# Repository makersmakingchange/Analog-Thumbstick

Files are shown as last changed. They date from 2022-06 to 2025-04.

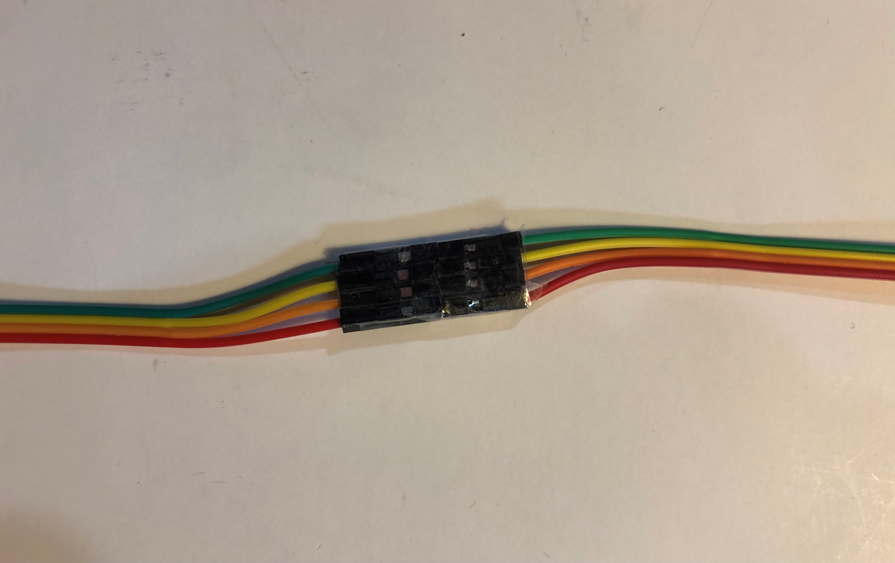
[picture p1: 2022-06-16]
Photos/taped wires.jpg

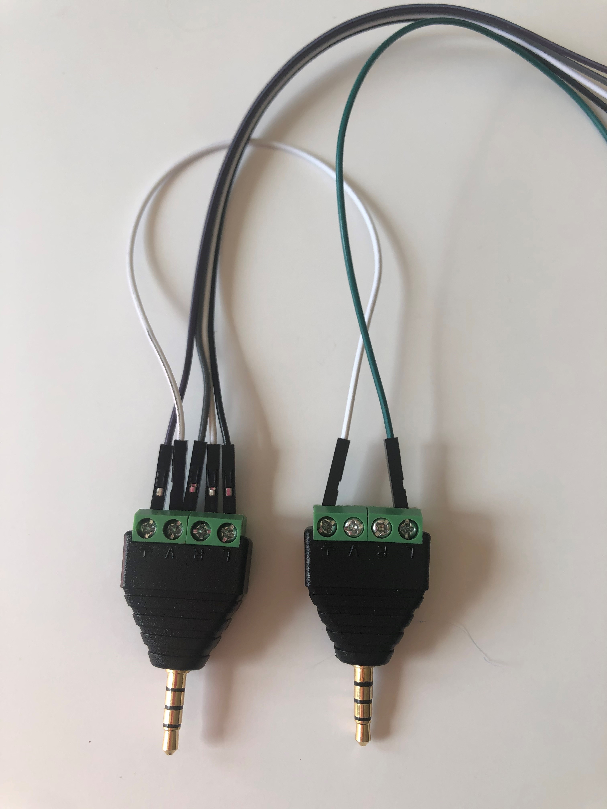
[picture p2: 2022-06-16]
Photos/blue - 2 monojacks.jpg

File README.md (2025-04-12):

# Analog Thumbstick
An analog thumbstick that can be used with the Xbox Adaptive Controller (XAC)



## More info at
- [Makers Making Change Project Page](https://makersmakingchange.com/?post_type=project&p=14952&preview=true)

## Getting Started
1. How to build this device

All of the files and instructions required to build the Low Profile Switch are contained within this repository. Refer to the Maker Checklist below.

2. How to request a build of this device

If you would like to obtain an Analog Joystick but do not have the skills or equipment to do so, you may submit a build request through the [MMC Library Page](https://makersmakingchange.com/project/low-profile-switch/). The requestor is responsible for the cost of materials and any shipping.

3. How to build this device for someone else

If you have the skills and equipment to build this device, and would like to donate your time to create the switch for someone who needs it, visit the [MMC Maker Wanted](https://makersmakingchange.com/maker-wanted/) section.

## Files

### Documentation
| Document             | Version | Link                                                                                  |
|----------------------|---------|---------------------------------------------------------------------------------------|
| Maker Checklist      | 1.0     | [Maker Checklist](/Documentation/Analog_Thumbstick_Maker_Checklist.pdf)         |
| Bill of Materials    | 1.0     | [BOM](/Documentation/Working_Documents/Analog_Thumbstick_BOM.xlsx)                                |
| 3D Printing Guide    | 1.0     | [3D Printing Guide](Documentation/Analog_Thumbstick_3D_Print_Guide.pdf)      |
| Assembly Guide       | 1.0     | [Assembly Guide](/Documentation/Analog_Thumbstick_Assembly_Guide.pdf)           |  
| Design Rationale     | 1.0     | [Design Rationale](/Documentation/Analog_Thumbstick_Design_Rationale.pdf)       |
| User Quick Guide     | 1.0     | [User Guide](/Documentation/Analog_Thumbstick_User_Guide.pdf)                  |

## Attribution 

3D printed joystick housing designed by Kerilyn Kennedy - Makers Making Change, inspired by Ron Nelson.

Documentation created by Neil Squire / Makers Making Change.

## License 
Everything needed or used to design, make, test, or prepare the Low Profile Switch is licensed under the CERN 2.0 Permissive license <https://ohwr.org/project/cernohl/wikis/Documents/CERN-OHL-version-2> (CERN-OHL-P) . 

Accompanying material such as instruction manuals, videos, and other copyrightable works that are useful but not necessary to design, make, test, or prepare the Low Profile Switch are published under a Creative Commons Attribution-ShareAlike 4.0 license <https://creativecommons.org/licenses/by-sa/4.0/> (CC BY-SA 4.0) 

 ----
<!-- ABOUT MMC START -->
## About Makers Making Change
[Makers Making Change Logo](https://www.makersmakingchange.com/)

Makers Making Change is a program of [Neil Squire](https://www.neilsquire.ca/), a Canadian non-profit that uses technology, knowledge, and passion to empower people with disabilities.

Makers Making Change leverages the capacity of community based Makers, Disability Professionals and Volunteers to develop and deliver affordable Open Source Assistive Technologies.

 - Website: [www.MakersMakingChange.com](https://www.makersmakingchange.com/)
 - GitHub: [makersmakingchange](https://github.com/makersmakingchange)
 - Bluesky: [@makersmakingchange.bsky.social](https://bsky.app/profile/makersmakingchange.bsky.social)
 - Instagram: [@makersmakingchange](https://www.instagram.com/makersmakingchange)
 - Facebook: [makersmakechange](https://www.facebook.com/makersmakechange)
 - LinkedIn: [Neil Squire Society](https://www.linkedin.com/company/neil-squire-society/)
 - Thingiverse: [makersmakingchange](https://www.thingiverse.com/makersmakingchange/about)
 - Printables: [MakersMakingChange](https://www.printables.com/@MakersMakingChange)

### Contact Us
For technical questions, to get involved, or to share your experience we encourage you to [visit our website](https://www.makersmakingchange.com/) or [contact us](https://www.makersmakingchange.com/s/contact).
<!-- ABOUT MMC END -->

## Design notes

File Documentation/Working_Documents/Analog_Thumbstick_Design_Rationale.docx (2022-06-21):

# Introduction

There is an identified need for cost-effective analog joysticks that can be used with the Xbox Adaptive Controller (XAC). There are currently not very many commercial joysticks on the market, and the ones that are can be costly. A joystick is required to play several games using the XAC as many users find it too challenging to use 4 switches as the alternative. This joystick is intended to be used with the XAC for anyone who may find it easier to game with a joystick.

# Research

## Commercial Joysticks:

Name | Price | Link | Picture

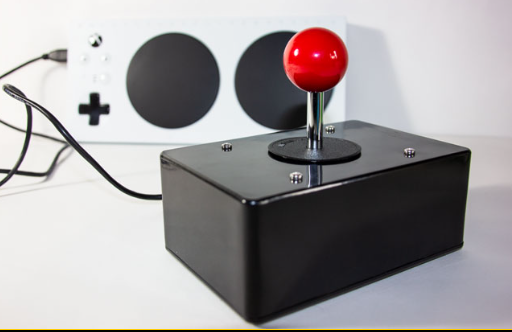
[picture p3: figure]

Ultra-Stik | 95 UK | Accessible Gaming Shop - Ultra-Stik - OneSwitch.org.uk (https://www.oneswitch.org.uk/art.php?id=17)

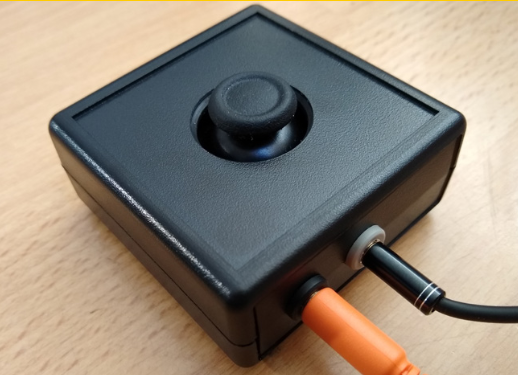
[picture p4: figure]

XAC MINI Stick | 105 UK | XAC Mini Joystick - OneSwitch.org.uk (https://www.oneswitch.org.uk/art.php?id=270)

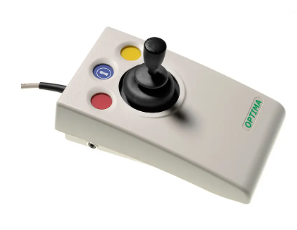
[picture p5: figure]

Optima Joystick | 219.60 UK | Optima Joystick - Video Gaming Assistive Joystick (pretorianuk.com) (https://www.pretorianuk.com/optima-joystick)

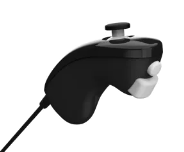
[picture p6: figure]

PDP One-Handed Joystick for Xbox Adaptive Controller | Out of Stock | PDP One-Handed Joystick for Xbox Adaptive Controller (microsoft.com) (https://www.microsoft.com/en-ca/d/pdp-one-handed-joystick-for-the-xbox-adaptive-controller/8qhw8mlwpp1l)
XAC Flat Thumbstick | $74.95 | XAC Flat Thumbstick (evilcontrollers.com) (https://www.evilcontrollers.com/xac-flat-thumbstick)

## DIY Joysticks:

Name | Price | Link | Picture

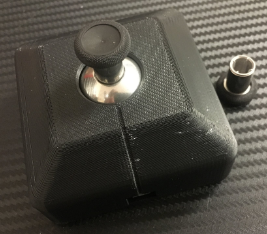
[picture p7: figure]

MINISTIX-TU | $75 | MINISTIX-TU (USB Version) — Warfighter Engaged (https://warfighterengaged.org/shop/ministix-tu)

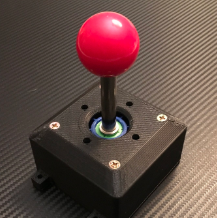
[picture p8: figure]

DPAD-T | $65 | DPAD-T — Warfighter Engaged (https://warfighterengaged.org/shop/dpad-t)

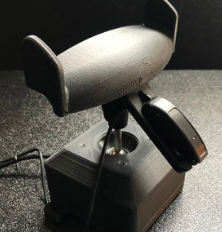
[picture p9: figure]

JOYSTIX-FPS | $75 | JOYSTIX-FPS — Warfighter Engaged (https://warfighterengaged.org/shop/joystix-l-aenef)

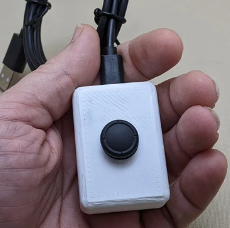
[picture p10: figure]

JoyCon® Style Joystick For XBOX® Adaptive Controller & PC (JoyToKey) | $60.40 | Joycon® Style Joystick for XBOX® Adaptive Controller & PC | Etsy Canada (https://www.etsy.com/ca/listing/1205880837/joycon-style-joystick-for-xbox-adaptive?click_sum=ba40a784&crt=1)

# Requirements

## Goals

G01 | To design a joystick compatible with the Xbox Adaptive Controller.
G02 | That the joystick is cost effective.

## Functional Requirements

F01 | That the joystick could accommodate different shaped toppers.
F02 | The joystick should be able to be used with a low activation force
F03 | Keeping the height of the base of the joystick to a minimum.

# Ideation

## Joystick

The inspiration for this device came from one of Ron Nelson’s joysticks online. The joystick shown below is compatible with the Xbox Adaptive Controller. As you can see, this joystick is mounted in a 3D printed nun chuck shape housing. For this project, it was decided to expand on Ron’s joystick design and design a rectangular 3d printed housing for the joystick so it would be able to lay flat on a surface easier and could potentially be used with Velcro.

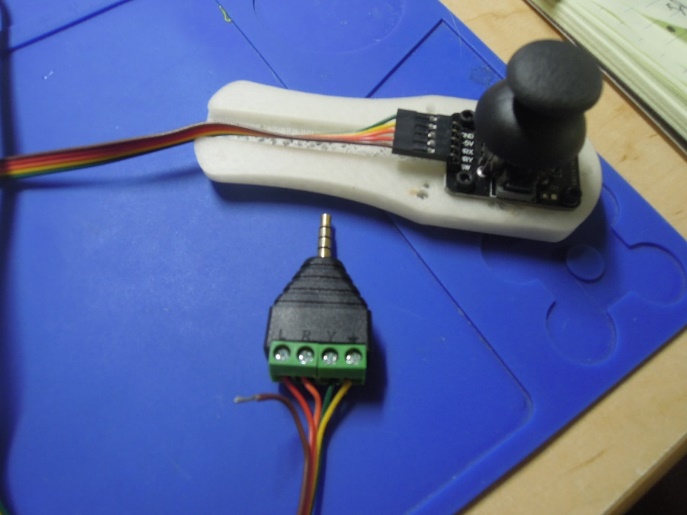
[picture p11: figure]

## Joystick Topper

The inspiration for having a U-shaped topper for the joystick came from one of the participants in our Adaptive Gaming Pilot Project. This participant uses a similar shaped topper on the joystick that operates their wheelchair and thought it would be beneficial to them. They mentioned that the thumbstick topper being used for our joystick would be too small and difficult for them to use. Rather than designing one from scratch, it was thought to modify one that currently exists to fit the required joystick.

# Conceptual Design

## Joystick Housing

The initial concept for the joystick housing was to design a rectangular 3D printed housing to mount the joystick in. It was decided to print the housing in two pieces to eliminate the need for printing with any supports. The two halves are attached together using four #4 1/2” screws – one in each corner. There are walls connecting the screw holes to the outside edge of the housing for reinforcement. Four of the same screws are also used to attach the joystick to the centre of the housing base. The biggest flaw in the first design was that the two walls in the middle of the base that were holding up the joystick snapped off once the joystick was screwed in. This was partially because the screw holes were initially too small, but more likely because there was no support perpendicular to the direction of the wall. The walls were thin and broke very easily when any rotational force was applied.

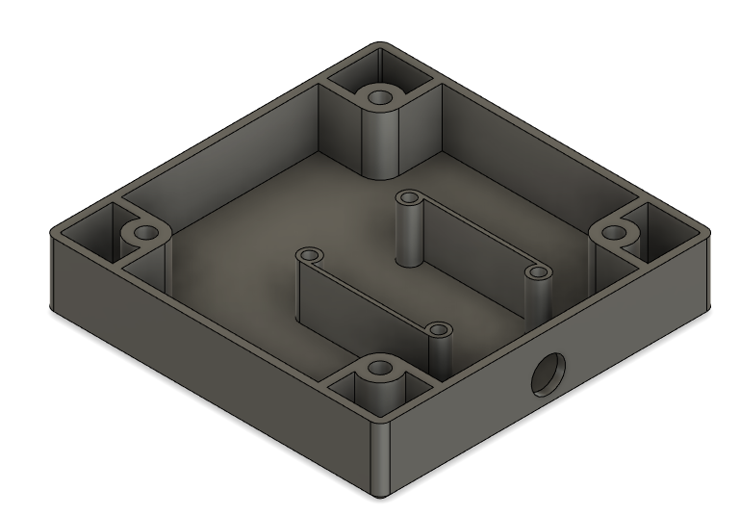
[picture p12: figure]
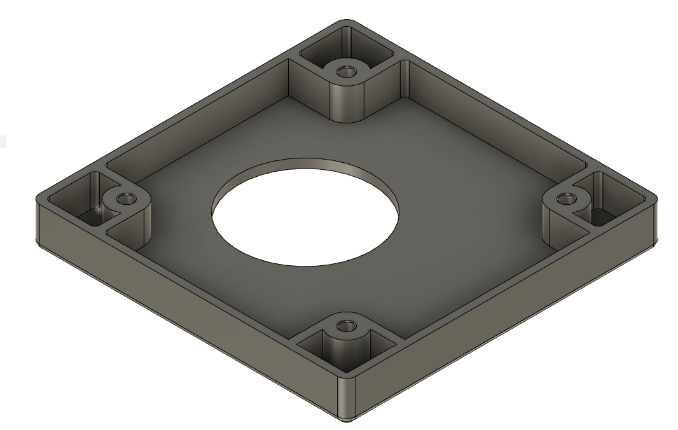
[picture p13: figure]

Bottom | Top (flipped over)

## Joystick Topper

It was thought to modify the joystick topper shown below, which was designed by EgonHeuson. The goal was to modify the base of the topper so that it was compatible with the joystick used.

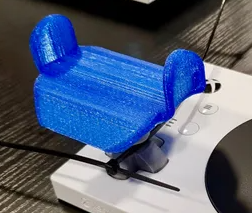
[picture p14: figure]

# Prototyping

Prototyping was used to make sure the joystick was centered with the hole in the top of the housing. Initial prototypes identified that the joystick needed to be slightly moved to achieve this. Prototyping was also used to determine how tall the housing must be to fit the 1/2" screws. Initial prototypes had the screws slightly poking up into the top of the housing, so adjustments were made to fix this. Prototyping was also used to determine an appropriately sized hole in the base for the wires to go through.

# Detailed Design

The analog thumbstick used in this project is compatible with the Xbox Adaptive Controller. There are 2 different versions of the joystick offered: one with the “press down” option (1), and one without (2). The press down function on the joystick is activated by pressing down on the top of the joystick. This function is used in some games, but not most. For this particular joystick, it requires a moderate amount of force to do so. An alternative to using the press down function of the joystick would be to map that function to a different switch. It was decided to offer both versions of the joystick as it is an easy add on if requested by the user.

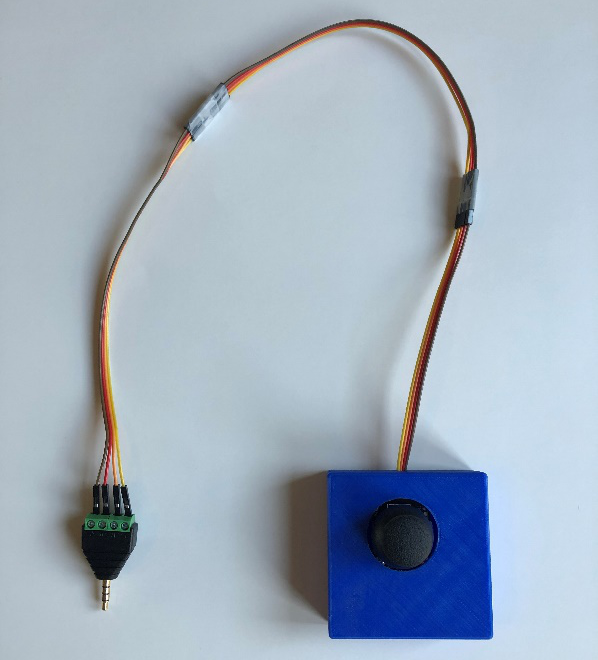
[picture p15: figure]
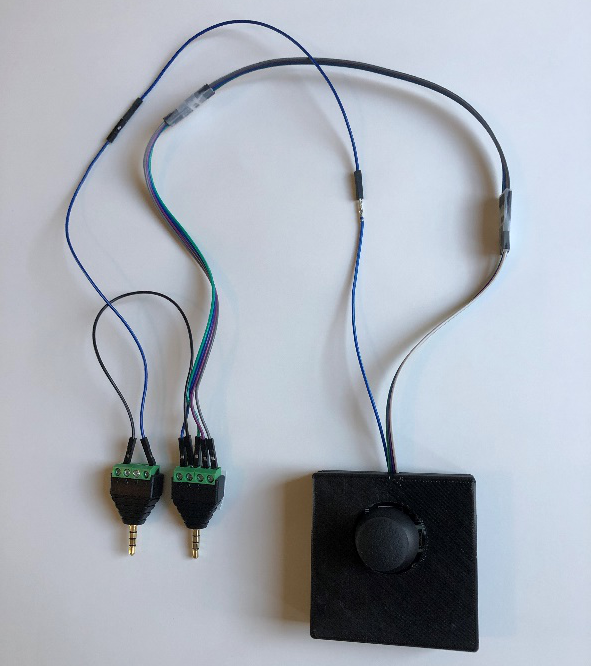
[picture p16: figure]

1. Analog Joystick without Pressdown Feature | 2. Analog Joystick with Pressdown Feature

The housing for the joystick was designed in 2 parts: the top and the base. This model is fairly similar to the enclosure previously described in Concept One. The following were key improvements that were made between iterations of 3D printed enclosures:

- Increasing wall strength where the joystick gets screwed into.
- Optimized the joystick hole size and joystick positioning to align with this hole.
- Modified the height of both 3D printed pieces to work with the 1/2" screws used to hold the enclosure together.

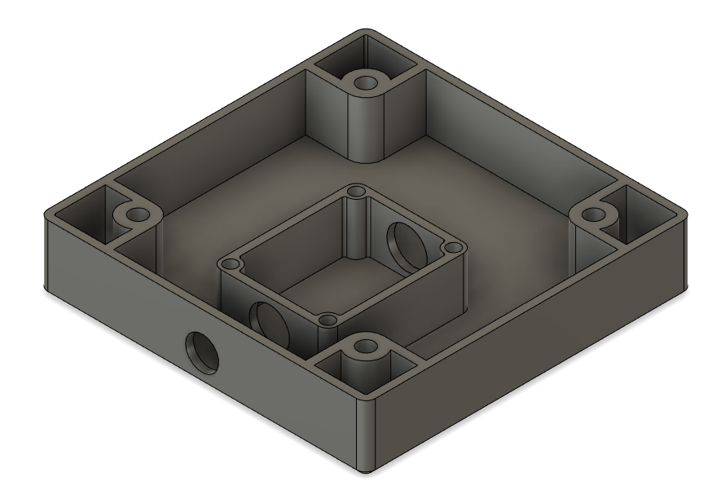
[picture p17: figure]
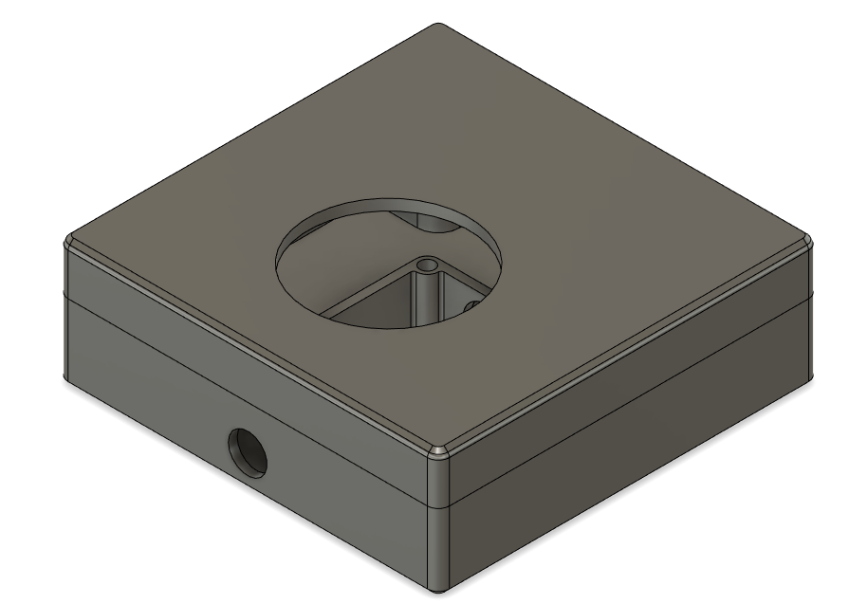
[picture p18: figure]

Bottom | Top

## Joystick Topper

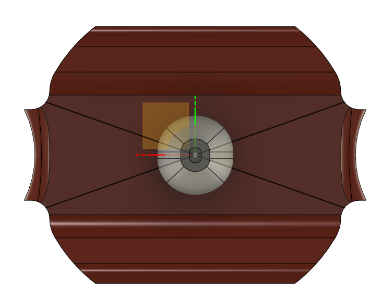
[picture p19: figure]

The U-shaped joystick topper was designed by modifying the base of the original joystick topper by EgonHeuson. The joystick topper was modified by adding a new base to it that would connect to the PS2 joystick used in this project.

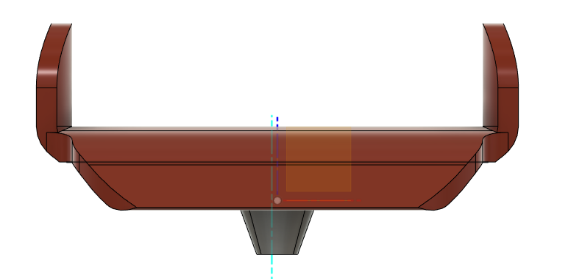
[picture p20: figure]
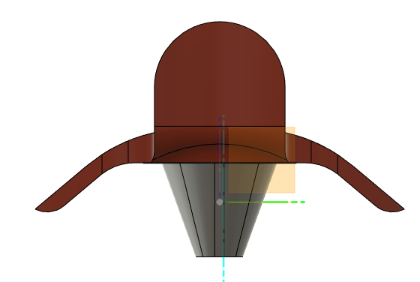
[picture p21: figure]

## Bottom

## Side

## Front

# Testing

The joystick was tested out by plugging it into the Xbox Adaptive Controller and connecting wirelessly to a computer. The online Gamepad Tester (https://gamepad-tester.com/) was used to test all the functions of the joystick. This could also be done by using the Xbox Adaptive controller on a gaming console and using the joystick to navigate the window.

# Opportunities for Improvement

- Minimizing the height of the joystick base.
- Snap fit between joystick top and base.
- Making the base more easily customizable (ex. possibly adding switches right into the base).
- Adding additional joystick toppers.

© 2022 by Neil Squire / Makers Making Change. This work is licensed under the CC BY SA 4.0 License: http://creativecommons.org/licenses/by-sa/4.0 Files available at https://makersmakingchange.com/project/analog-thumbstick/ Page 1 of 1

V1.0 | MAY 2022 Analog Thumbstick Design Rationale

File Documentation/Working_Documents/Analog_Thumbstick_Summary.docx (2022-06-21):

# Title

Analog Thumbstick

## Subtitle

An analog thumbstick that can be used with the Xbox Adaptive Controller (XAC)

## Device Specifications

Build Time:

< 1hr

1-4 hr

5-10hr

>10hr

Cost:

$0 - $10

$11 - $25

$26 - $50

$51 - $100

$101 - $250

$250+

Stage: Recently Added

Skills: Mechanics, 3D Printing

Need: Mobility

Disability: Mobility/Physical

Difficulty: Intermediate

License: Attribution-ShareAlike 4.0 International

Usages: Mobility, Computer Access, Recreation and Leisure

Type: Gaming

Designer: 3D printed joystick housing designed by Kerilyn Kennedy - Makers Making Change, inspired by Ron Nelson.

## Device Details

### Overview

This is a cost-effective analog thumbstick intended to be used for adapted gaming with the Xbox Adaptive Controller (XAC). This device is a more affordable option to commercial thumbsticks on the market. This thumbstick is easy to use and gets plugged into the jacks in the back of the XAC. The design is based on a traditional PS2 thumbstick that is mounted into a 3D printed housing. The original plastic joystick topper can be swapped out for a 3D printed "U" shaped topper to make it easier to use.

### Usage

The Analog Thumbstick is connected to the XAC by plugging the TRRS plug into the "X1 " or " X2" jack on the back of the controller. If so equipped, the optional “push button” feature is connected by plugging into the is enabled on the thumbstick, a second jack will be plugged into the "L" or "R" port that look like joystick icons. The joystick can also be used with the "U" shaped topper. This may be beneficial to someone who may not have the dexterity to use a smaller joystick, or someone who may have limited sensation in their fingers but still has enough wrist movement to use a joystick.

## Compatibility

This joystick is compatible with the Xbox Adaptive controller. The XAC can be used with any Xbox Series X|S or Xbox One, any Windows PC game that supports the Xbox Adaptive Controller, as well as other gaming consoles with an appropriate adapter.

### Cost

The thumbstick costs approximately $30 to build. Note, the device can be built for cheaper if more than one is ordered as several of the parts for this device come in larger quantities than needed for one device.

### Build Instructions

A set of build instructions can be found in the assembly guide that is linked above.

#### Skills Required

- 3D Printing
- Mechanics

#### Time Required

3D Printing Time:

Joystick Housing: 2:47

U-shaped Topper: 4:22

Assembly Time: 10 minutes

#### Tools

- Small Flat Headed Screwdriver
- Tape

#### Components

- 1x Joystick
- 16x Dupont Wires
- 2x Headphone Plugs - only one is needed if the "push button" feature of the joystick is not requested.
- 8x #4 1/2" screws

#### 3D Printing

- Joystick Top
- Joystick Base

All components can be printed with no support at 20% infill with a 0.2mm layer height. 3D print files are linked above.

### Attribution

3D printed joystick housing designed by Kerilyn Kennedy - Makers Making Change, inspired by Ron Nelson.

Documentation created by Neil Squire / Makers Making Change.

© 2022 by Neil Squire / Makers Making Change. This work is licensed under the CC BY SA 4.0 License: http://creativecommons.org/licenses/by-sa/4.0 Files available at https://makersmakingchange.com/project/analog-thumbstick/ Page 1 of 1

V1.0 | MAY 2022 Analog Thumbstick Summary

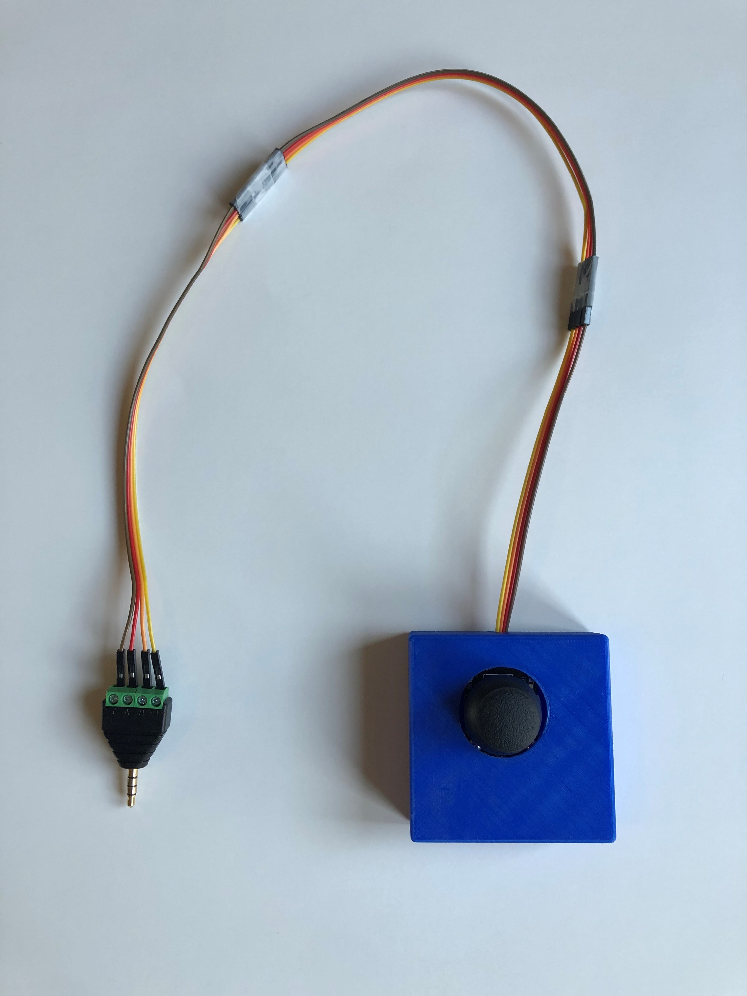
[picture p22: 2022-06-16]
Photos/one mono jack.jpg

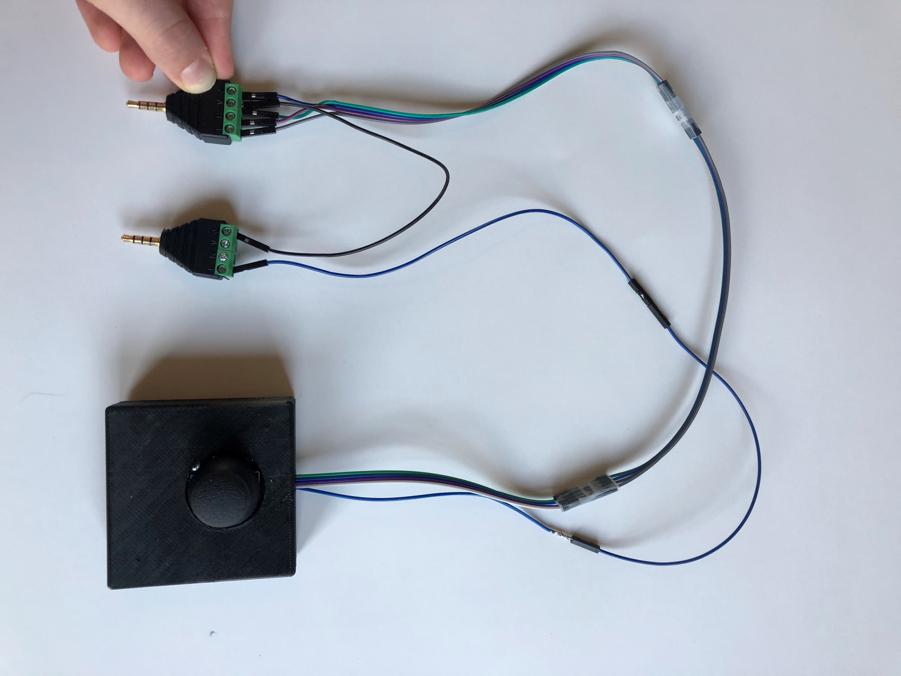
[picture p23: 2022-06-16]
Photos/Joystick with 2 monojacks.jpg

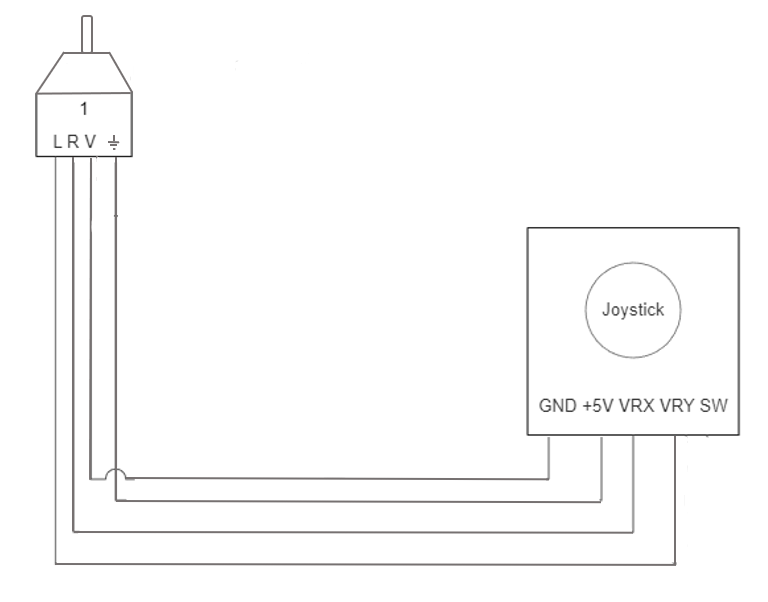
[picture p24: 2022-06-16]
Photos/wire diagram without press dwon function.PNG

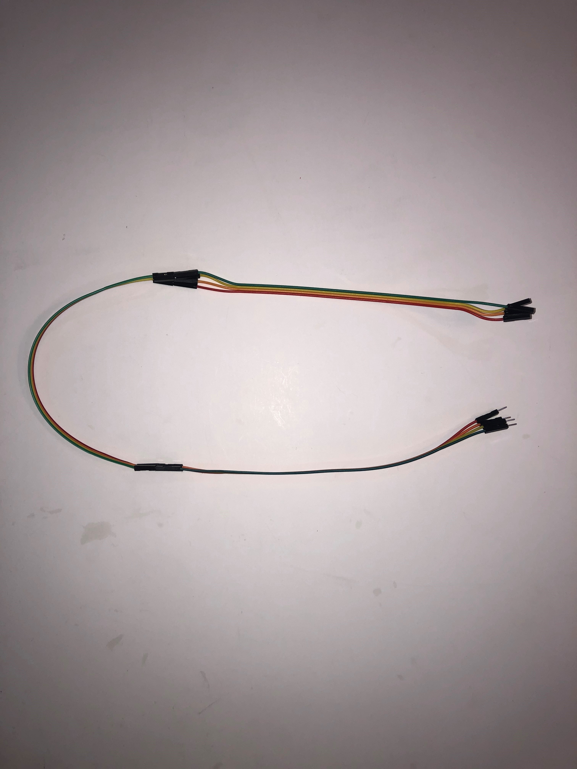
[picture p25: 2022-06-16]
Photos/dupont wires connected.jpg

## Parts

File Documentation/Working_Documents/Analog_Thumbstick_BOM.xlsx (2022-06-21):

Device: Analog Thumbstick | Date: May 31, 2022 | Thumbstick without Pressdown Function Cost | Total Print time (hr) | Total filament (g)
Version: V1.0 |  | $18.13 | 2.78 | 39
 |  | Thumbstick with Pressdown Function Cost
 |  | $22.10
Commercial Parts:
Part type (Electrical. Mechanical, Sanitization, ect) | Part Name | Quantity Needed | Pkg Quantity | Price per package | Price per Unit | Price for qty needed | Link
Analog Thumbstick Without Pressdown Function
#4 1/2" screws | 9018940 | 8 | 75 | $8.22 | $0.11 | $0.88 | https://www.amazon.ca/Prime-Line-9018940-Self-Tapping-Phillips-Plated/dp/B074ZXK788?rnid=12035759011
Joystick | ‎C96554ec28bcda7d5790cfeb7407f978 | 1 | 1 | $9.99 | $9.99 | $9.99 | https://www.amazon.ca/DOLITY-Joystick-Controller-Breakout-Analogue/dp/B07GS5RZ4B
Dupont Wires | a13040500ux0203 | 12 | 120 | $9.87 | $0.08 | $0.99 | https://www.amazon.ca/gp/product/B01M1IEUAF/ref=ppx_yo_dt_b_asin_title_o08_s00?ie=UTF8&psc=1
Headphone Plug |  | 1 | 1 | $5.30 | $5.30 | $5.30 | PULABO4-Pole 3.5mm Headphone Plug Male to AV 4 Pin Solderless Shield Terminal Cable(Black) Useful and Fashion : Amazon.ca: Electronics (https://www.amazon.ca/PULABO4-Pole-Headphone-Solderless-Terminal-Fashion/dp/B09TP4YM92?rnid=12035759011&s=electronics)
Analog Thumbstick With Pressdown Function
#4 1/2" screws | 9018940 | 8 | 75 | $8.22 | $0.11 | $0.88 | https://www.amazon.ca/Prime-Line-9018940-Self-Tapping-Phillips-Plated/dp/B074ZXK788?rnid=12035759011
Joystick | ‎C96554ec28bcda7d5790cfeb7407f978 | 1 | 1 | $9.99 | $9.99 | $9.99 | https://www.amazon.ca/shamjina-Dual-Joystick-Module-Rocker/dp/B08CRC15B6?rnid=12035759011
Dupont Wires | a13040500ux0203 | 16 | 120 | $9.87 | $0.08 | $1.32 | https://www.amazon.ca/gp/product/B01M1IEUAF/ref=ppx_yo_dt_b_asin_title_o08_s00?ie=UTF8&psc=1
Headphone Plug |  | 2 | 2 | $8.94 | $4.47 | $8.94 | https://www.amazon.ca/gp/product/B07FQFFPL6/ref=ppx_yo_dt_b_asin_image_o05_s00?ie=UTF8&psc=1
3D Printed Parts ESTIMATED PRICING USING 1KG ROLL COST: | $25.00
Part | Description | Quantity Needed | TOTAL Mass (g) | Estimated Price | Print Time (Min) | Link
Joystick_Top |  | 1 | 16 | $0.40 | 65
Joystick_Base |  | 1 | 23 | $0.57 | 102
 |  |  | Total Print Cost: | $0.97
Tools for Assembly
Small flat headed screw driver
Tape
Alternatives (if there are other sources for some parts link them below)
Part and description | Link
A lot of the parts for the joysticks can be found on Amazon in larger quantities if the user wants more than one
#4 1/2" screws can likely be found in smaller quantities at your local hardware store but typically require a No. 0 Robertson screw driver which is not as common
Headphone plug used in the assembly guide - I don’t think they sell them individually. | https://www.amazon.ca/gp/product/B07FQFFPL6/ref=ppx_yo_dt_b_asin_image_o05_s00?ie=UTF8&psc=1
The one linked above works the same but looks a little different.
10 Joysticks for $21: | WMYCONGCONG 10 PCS Joystick Breakout Module Game Controller for Arduino PS2 : Amazon.ca: Electronics (https://www.amazon.ca/WGCD-Joystick-Breakout-Controller-Arduino/dp/B01N59MK0U?s=electronics)
3 Joysticks for $11: | Pack of 3Pcs Joystick Game Controller Breakout Module for PS2 Arduino Board Analogue : Amazon.ca: Electronics (https://www.amazon.ca/DOLITY-Joystick-Controller-Breakout-Analogue/dp/B07GS5RZ4B)

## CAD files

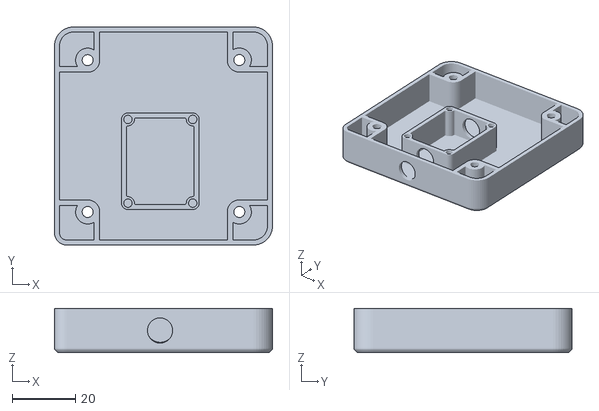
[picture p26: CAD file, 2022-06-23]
Build_Files/joystick_base.stl
69.0 x 69.0 x 14.0

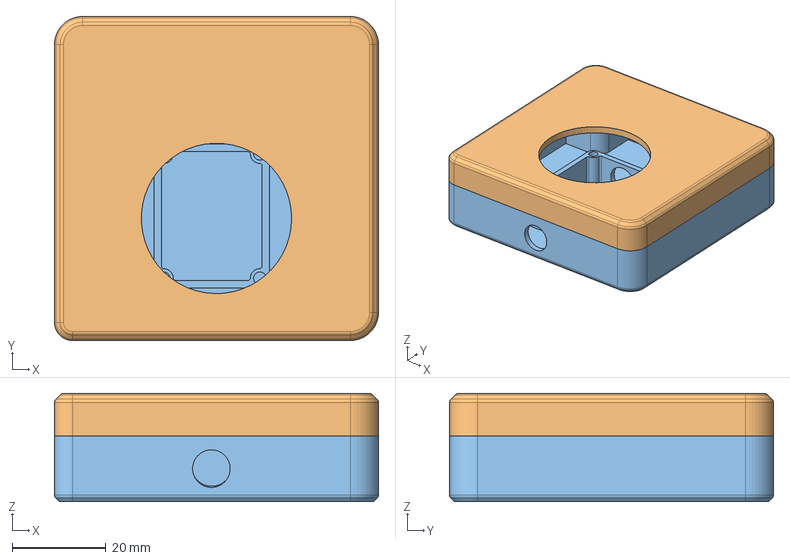
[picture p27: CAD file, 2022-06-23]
Design_Files/Analog_Thumbstick.step
69.0 x 69.0 x 23.0 mm
Bottom
Top
Prongs for joystick

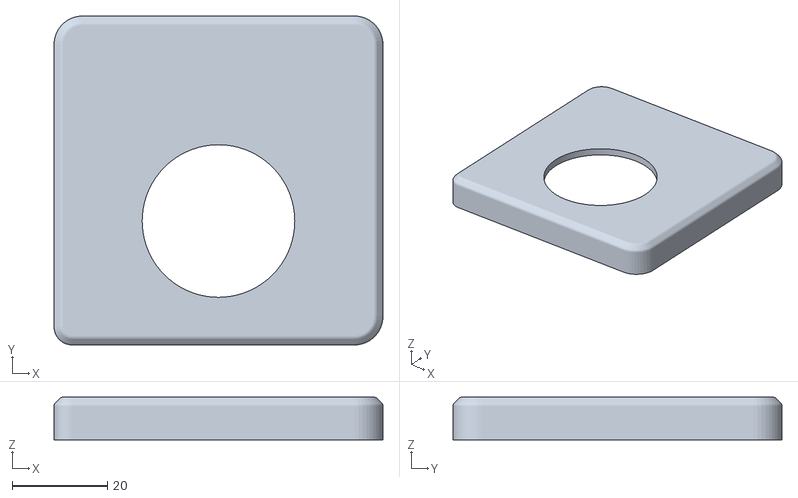
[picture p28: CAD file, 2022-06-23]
Build_Files/joystick_top.stl
69.0 x 69.0 x 9.00

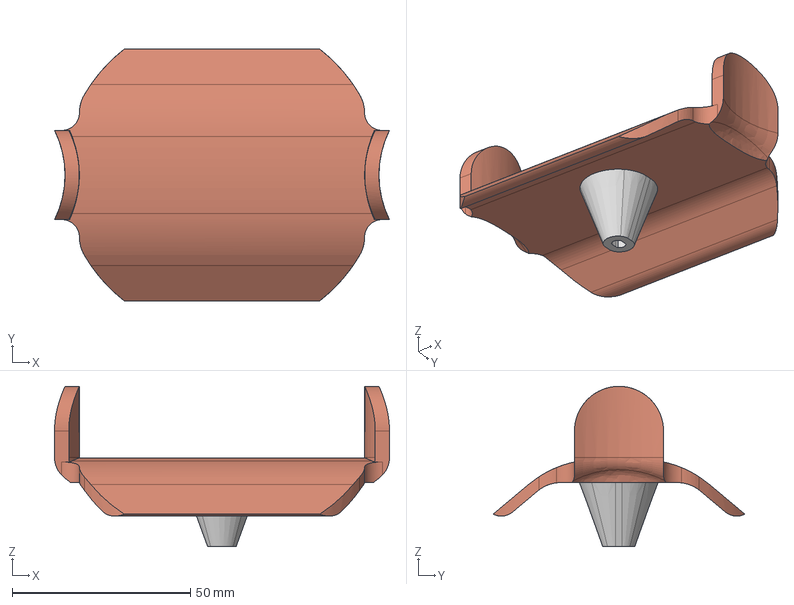
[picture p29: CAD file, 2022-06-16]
Design_Files/U-shaped_Joystick_Topper.step
94.0 x 70.6 x 45.0 mm
Joystick topper base
XAC_HandiAdapter_JoyStick_ErgoDesign

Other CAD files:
Build_Files/U-shaped_Joystick_Topper.stl
Design_Files/Analog_Thumbstick.f3d
Design_Files/U-shaped_Joystick_Topper.dwg

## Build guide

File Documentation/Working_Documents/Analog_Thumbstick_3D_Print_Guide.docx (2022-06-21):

# 3D Printing Summary

Metrics | Joystick
Total Print Time (min) | 167
Total Number of Components | 2
Typical Total Mass (g) | 39
Typical Number of Print Setups | 1

# 3D Printing Settings

Print File Name | Qty | Total Print Time (hr:min) | Mass (g) | Infill (%) | Support (Y/N) | Layer Height/ Nozzle Diameter(mm) | Notes (orientation, special settings, etc)
joystick_top.stl | 1 | 1:05 | 16 | 20 | N | 0.2/0.4 | Print in orientation given in STL
joystick_base.stl | 1 | 1:42 | 23 | 20 | N | 0.2/0.4 | Print in orientation given in STL
U-shaped_ Joystick_Topper.stl (If requested) | 1 | 4:22 | 45 | 20 | Y | 0.2/0.4 | Support plate on build plate only

# Post-Processing

The 3D printed joystick top and base print without supports. If the requestor wants the U-shaped Joystick Topper, it prints with supports that will have to be removed.

# Customization Options

The used can request the U-shaped joystick topper. They can also request that the device be printed in multiple colours.

# Examples of Quality Prints:

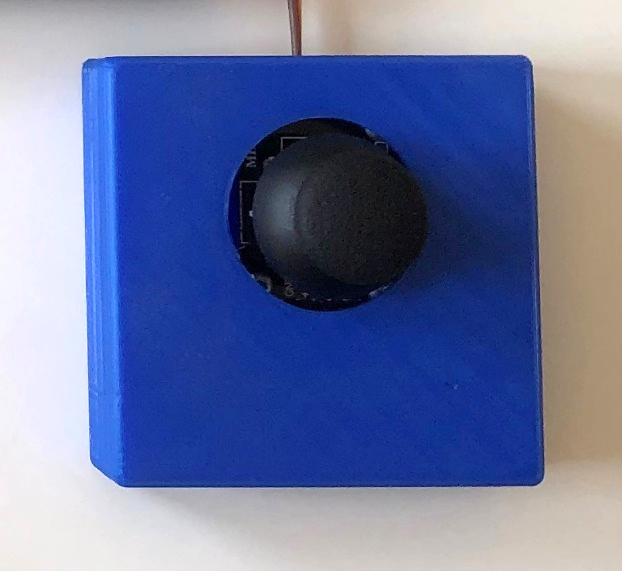
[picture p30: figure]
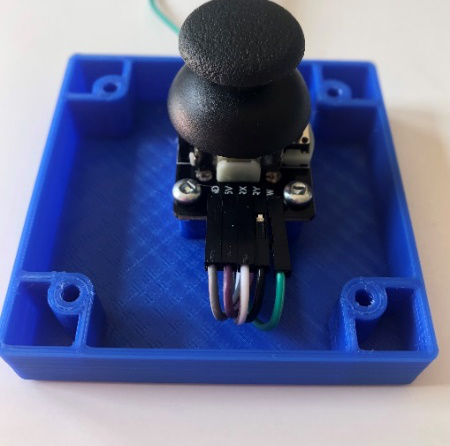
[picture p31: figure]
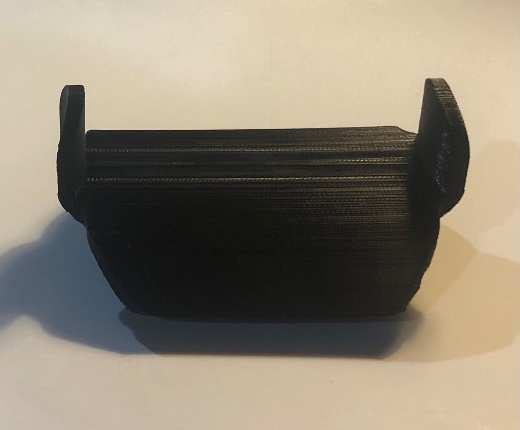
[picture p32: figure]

Top | Bottom | U-shaped Joystick Topper

© 2022 by Neil Squire / Makers Making Change. This work is licensed under the CC BY SA 4.0 License: http://creativecommons.org/licenses/by-sa/4.0 Files available at https://makersmakingchange.com/project/analog-thumbstick/ Page 1 of 2

V1.0 | MAY 2022 Analog Thumbstick 3D Printing Guide

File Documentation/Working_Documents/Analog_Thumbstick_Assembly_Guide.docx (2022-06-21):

# Required Components BOM

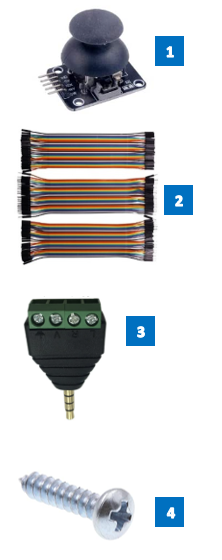
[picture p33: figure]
picture of joystick, dupont wires, headphone adapter, and screws required to build this device

| Thumbstick without Press Down Function 1. 1x PS2 Joystick 2. 12x Dupont Wires: 4 male/male, 4 male/female, 4 female/female – it is recommended that the same 4 colours are used for the different types of wires as they will be getting connected. 3. 1x Headphone Adapter 4. 8x #4 1/2" screws | Thumbstick with Press Down Function 1. 1x PS2 Joystick 2. 16x Dupont Wires: 6 male/male, 5 male/female, 5 female/female – it is recommended that the same 5 colours are used for the different types of wires as they will be getting connected. 3. 2x Headphone Adapters 4. 8x #4 1/2" screws

# Required Tools

- Small flat headed screwdriver
- Tape

## Assembly Instructions for the Analog Thumbstick without the Press Down Function – pg 2

## Assembly Instructions for the Analog Thumbstick with the Press Down Function – pg 5

Please refer to the Analog Joystick Maker Checklist to ensure you ask the user which version of the joystick they want.

# Assembly Instructions for Analog Thumbstick without the Press Down Function

## Step 1

Locate 12 dupont wires: 4 male – female, 4 male-male, 4 female-female. It is also recommended that you use the same colours for each of these different types of wires.

Male-Male

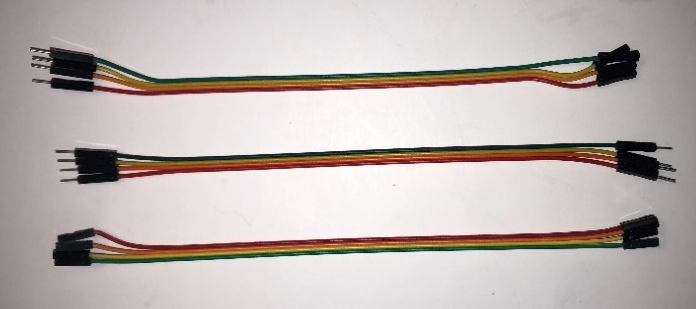
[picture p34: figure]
a picture of the 12 dupont wires that are going to be connected together in the next step

Male-Female

Female-Female

## Step 2

Connect the same colour wires so that you now have wires 3 lengths long, with one male end and one female end.

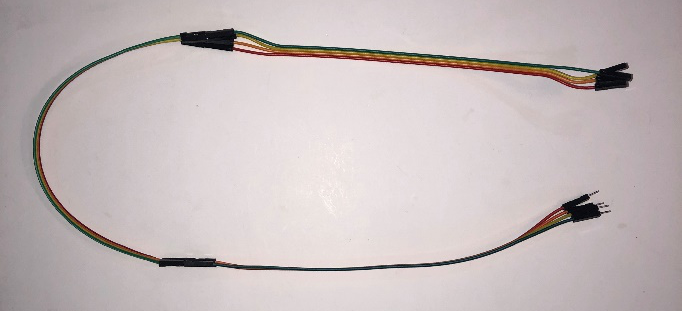
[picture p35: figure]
A picture of the dupont wires connected together

Female

Male

## Step 3

Use tape to secure the connected wires.

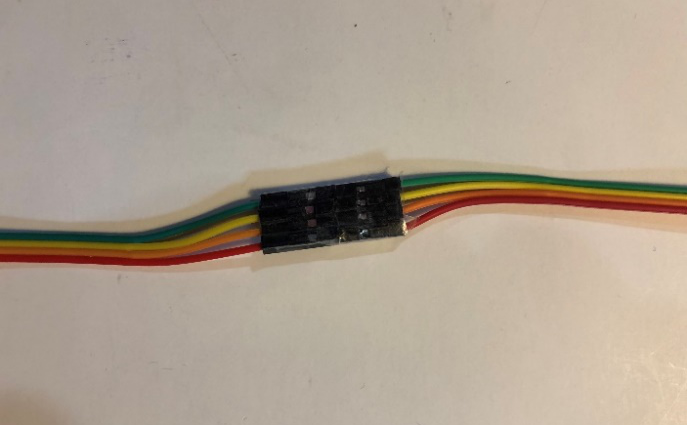
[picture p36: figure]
a picture of the ends of the dupont wires that are connected taped together

## Step 4

Feed the female end of the wires through the 3 holes in the 3D printed joystick base.

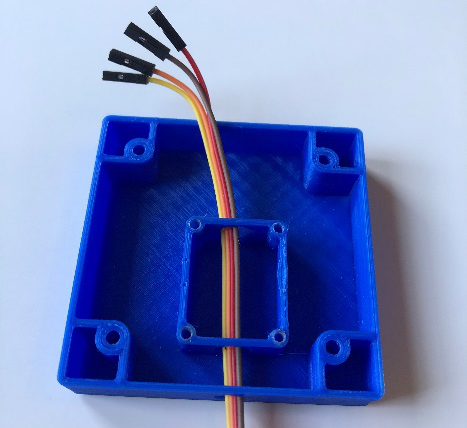
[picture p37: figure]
a picture weeding the wires though the holes in the 3d printed joystick base

## Step 5

Connect the wires to the GND, +5V, VRX, and VRY prongs on the joystick.

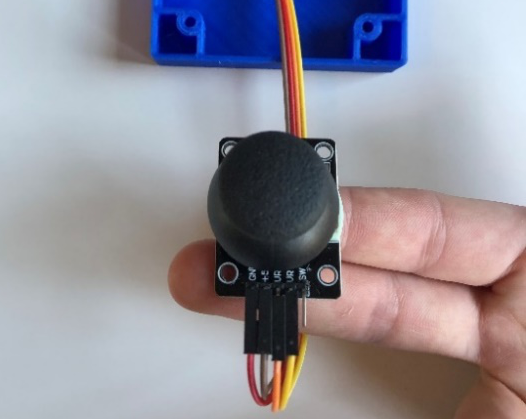
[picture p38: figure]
a picture showing the wires connected to the joystick

## Step 6

Connect the joystick to the 3D printed base with 4 screws.

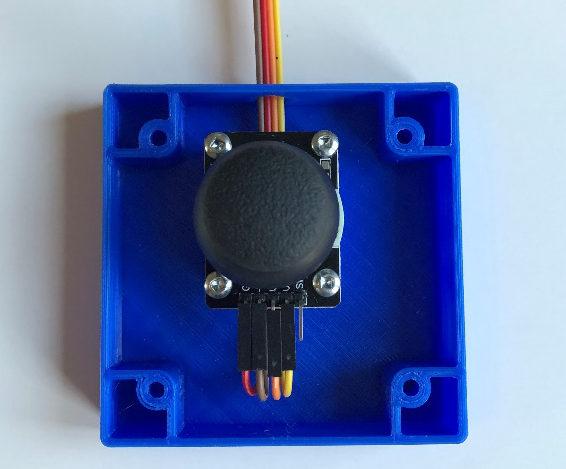
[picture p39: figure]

## Step 7

Loosen the 4 screws on the headphone adapter.

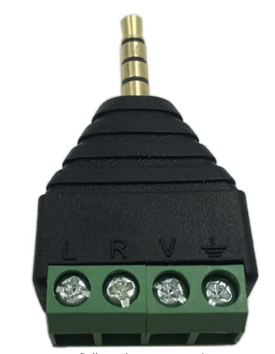
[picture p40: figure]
a picture of a green headphone adapter

## Step 8

Insert the male ends of the wires under the screws in the headphone adapter according to the diagram above. When inserted, tighten the screws to secure the wires.

A wire diagram of how to connect the wires from the headphone adpater to the joystick

## Step 9

This is what the device should look like thus far.

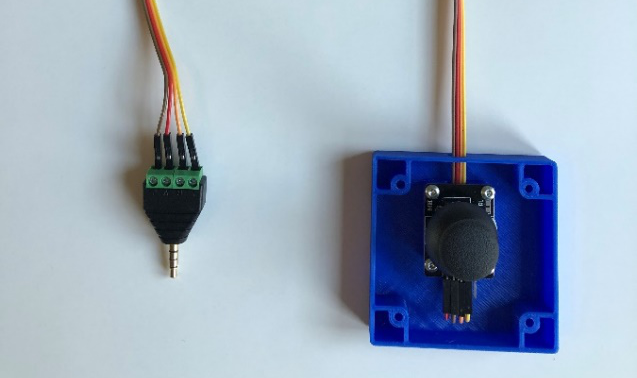
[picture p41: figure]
a picture of the joystick wired in the 3d printed base

## Step 10

Align the 3D printed top of the joystick with the base.

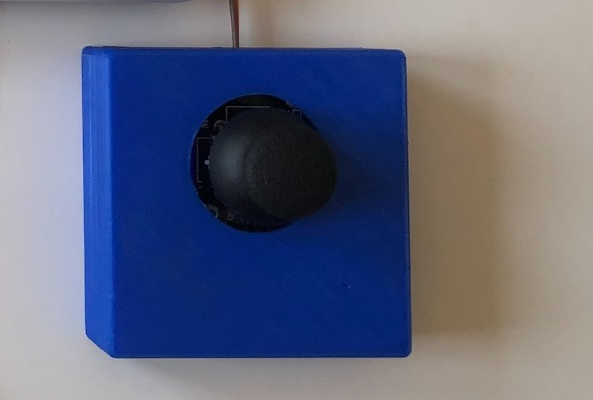
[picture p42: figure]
a picture of the 3d printed joystick base with the top added to it

## Step 11

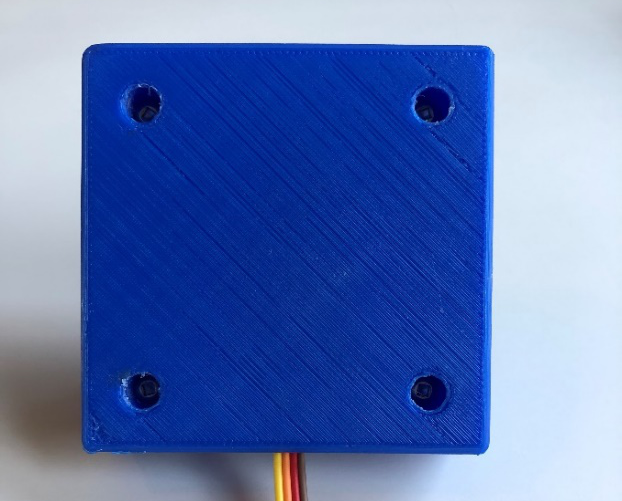
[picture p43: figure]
a picture of the bottom of the 3d printed joystick base with 4 screw holes

Insert 4 screws in the base of the joystick to hold the top and base together.

# Assembly Instructions for Analog Thumbstick with the Press Down Function

## Step 1

Locate 12 dupont wires: 4 male – female, 4 male-male, 4 female-female. It is also recommended that you use the same colours for each of these different types of wires.

Male-Male

Male-Female

Female-Female

## Step 2

Connect the same colour wires so that you now have wires 3 lengths long, with one male end and one female end.

Female

Male

## Step 3

Use tape to secure the connected wires.

## Step 4

Locate 3 more dupont wires: 1 male – female, 1 male-male, 1 and 1 female-female of the same colour. Connect and tape them to each other similar to steps 2 and 3.

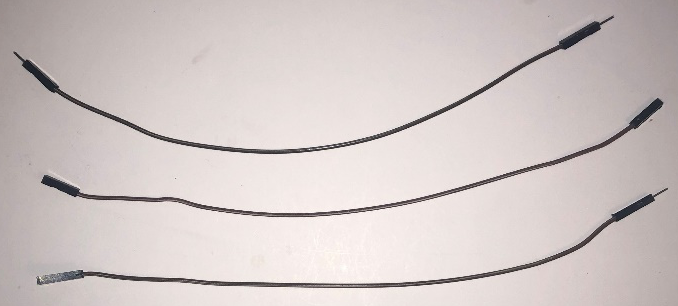
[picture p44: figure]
a picture of 3 more dupont wires

## Step 5

Feed the female end of the 5 wires through the 3 holes in the 3D printed joystick base.

## Step 6

Connect the group of 4 wires to the GND, +5V, VRX, and VRY prongs on the joystick. Connect the single 5th wire to the SW prong.

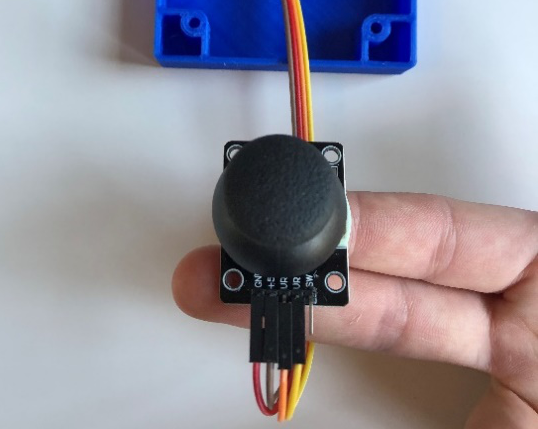
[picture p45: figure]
a picture showing the wires connected to the joystick

## Step 7

Connect the joystick to the 3D printed base with 4 screws.

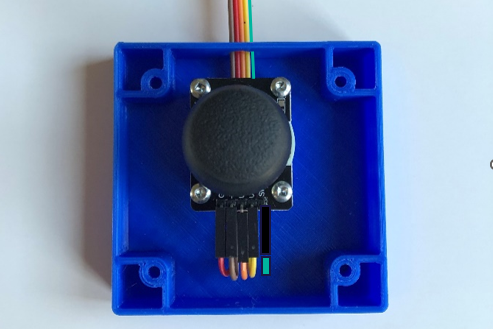
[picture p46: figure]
a picture of the joystick in the 3d printed base with 4 screws holding it down

## Step 8

Loosen the 4 screws on both of the headphone adapters.

## Step 9

Insert the male ends of the wires under the screws in the headphone adapters according to the diagram above. This will also require a single male-male Dupont wire to be used as shown above in addition to previously mentioned wires. When inserted, tighten the screws to secure the wires. Note: on headphone adapter 1, 2 wires will be going into the V port. This may be challenging but both wires should be able to be secured with one screw.

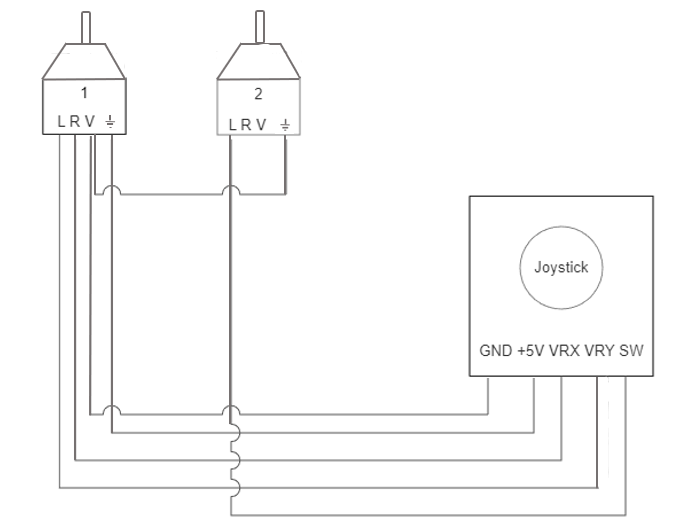
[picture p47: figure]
A wire diagram of how to connect the wires from the two headphone adpaters to the joystick

Wires from Step 2

Wire from Step 4

Single male-male Dupont wire

## Step 10

This is what the device should look like thus far.

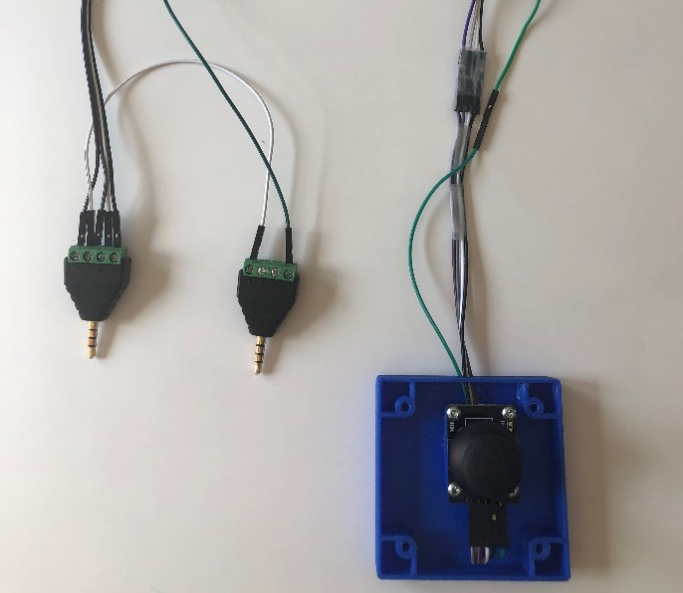
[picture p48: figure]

## Step 11

Align the 3D printed top of the joystick with the base.

## Step 12

Insert 4 screws in the base of the joystick to hold the top and base together.

© 2022 by Neil Squire / Makers Making Change. This work is licensed under the CC BY SA 4.0 License: http://creativecommons.org/licenses/by-sa/4.0 Files available at https://makersmakingchange.com/project/analog-thumbstick/ Page 1 of 1

V1.0 | MAY 2022 Analog Thumbstick Assembly Guide

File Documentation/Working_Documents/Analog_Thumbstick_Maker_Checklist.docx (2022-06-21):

# Maker To Do List

- Read through the Assembly Guide to become familiar with required components, tools, supplies, and safety gear and overall assembly steps.
- Ask the user if they want the “thumb stick click” option on the joystick. This function is activated by pressing down on the joystick. It is not used for all games but is an option for users to have. Note, it is relatively hard to press and the alternative to having it could be using an additional switch.
- Talk to User about customization options (e.g., color, any special requests, etc.)
- Order hardware components
- Gather tools, supplies, and safety equipment.
- Assemble the device. Double check it is wired correctly as the device cannot be tested without an Xbox Adaptive Controller (XAC). If you have an XAC, you can test the joystick here. (https://gamepad-tester.com/)
- Take pictures of the device wiring as shown below before sending off device. They might come in handy if the user tests out the device and it is not working as expected.

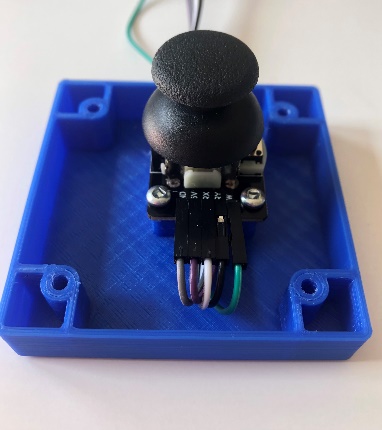
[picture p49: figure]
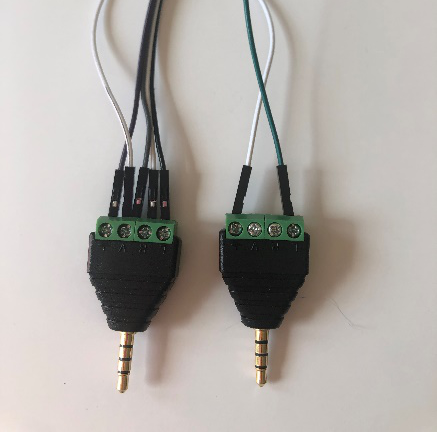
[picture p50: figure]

- Print Analog Thumbstick User Guide

# Items to Give to User

- Assembled Analog Thumbstick
- Analog Thumbstick User Guide

© 2022 by Neil Squire / Makers Making Change. This work is licensed under the CC BY SA 4.0 License: http://creativecommons.org/licenses/by-sa/4.0 Files available at https://makersmakingchange.com/project/analog-thumbstick/ Page 1 of 1

V1.0 | MAY 2022 Analog Thumbstick Maker Checklist

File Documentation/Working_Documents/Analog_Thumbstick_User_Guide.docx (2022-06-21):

## Introduction

This is a low-cost analog thumbstick that is compatible with the Xbox Adaptive Controller (XAC). This device is a more affordable option to commercial joysticks on the market. This joystick is easy to use and gets plugged into the back of the XAC.

## Features

The thumbstick sits into a 3D printed housing and was designed using a traditional PS2 joystick. The wiring connected to the joystick extends out to a headphone adapter that will be plugged into the XAC (1). The joystick will have two headphone adapters attached if the “press down” function on the joystick was requested by the user (2). Both thumbsticks shown below are displayed in their intended orientation with the wires coming out of the back of the thumbstick.

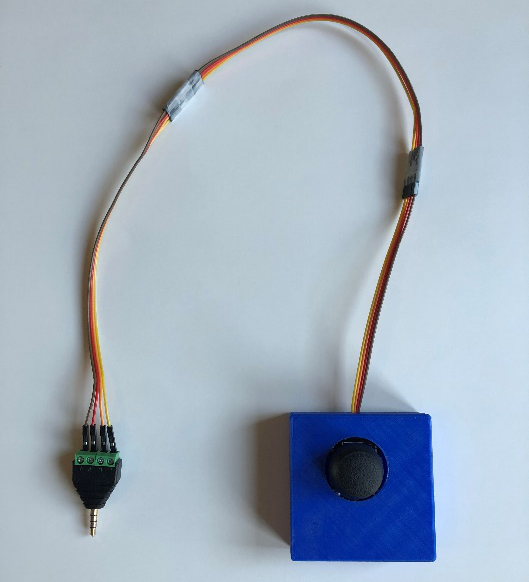
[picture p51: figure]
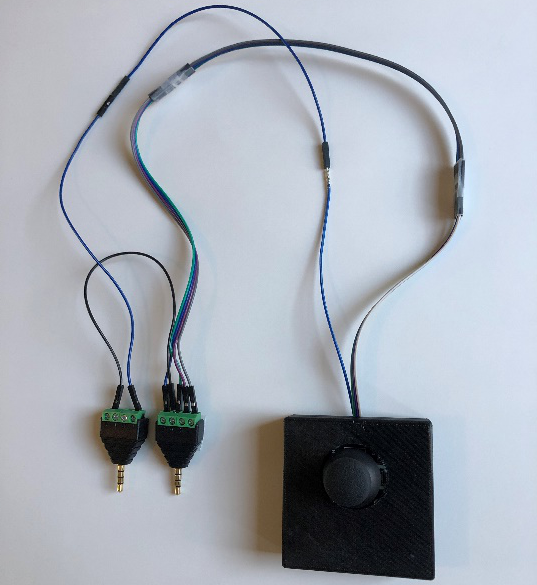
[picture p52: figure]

1 | 2

The thumbstick can either be used with a single finger with the original thumbstick topper (3), or the user can request a 3D printed "U" shaped topper that is typically used with more than one finger (4). This topper may be beneficial to someone who may have limited finger sensation but still has enough wrist movement to operate a joystick.

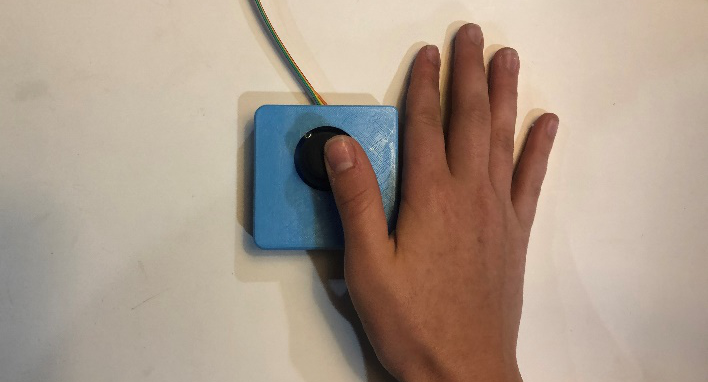
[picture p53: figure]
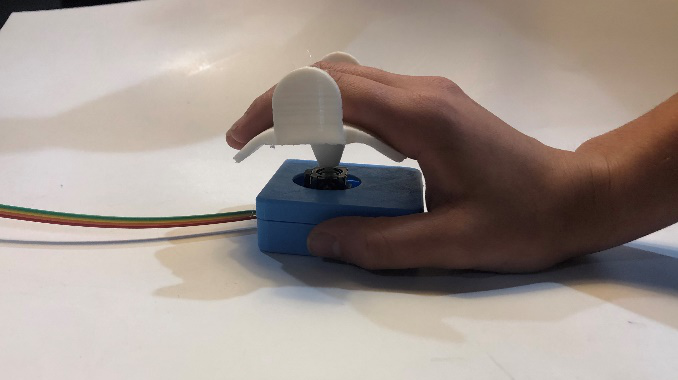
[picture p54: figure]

3 | 4

## Usage

This thumbstick is intended to be paired with an Xbox Adaptive Controller. The joystick can be used by plugging it into the "X1 " (5) or " X2" (6) jacks on back of the controller.

If it was requested that the “push button” feature is enabled on the joystick, the second jack (the one with less wires) can be plugged into the "L" (7) or "R" (8) mono jack that look like joystick icons as shown below.

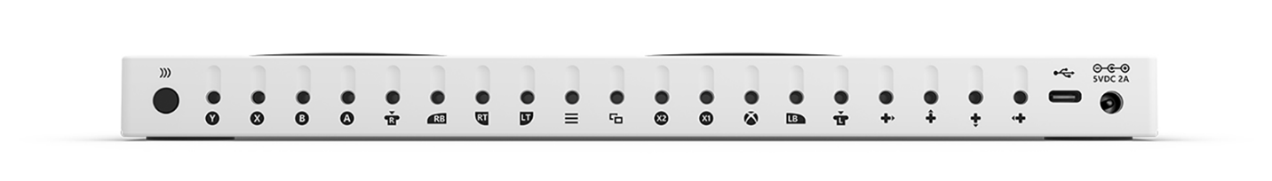
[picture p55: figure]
See the source image

8

7

6

5

## Compatibility

This thumbstick is compatible with the Xbox Adaptive controller. The XAC can be used with an Xbox Series X|S or Xbox One, Windows PC, iOS devices, Android mobile devices, as well as other gaming consoles with an appropriate adapter.

## How to Connect the Xbox Adaptive Controller to Your Device

Instructions on how to connect the Xbox Adaptive Controller to your device are linked below. Note, the XAC can connect to other consoles than the ones listed but an additional adapter may be required.

Device | Link
iOS | shorturl.at/dfsyY
Android | shorturl.at/aqvMN
Windows PC | shorturl.at/rxzFZ
Xbox | shorturl.at/cCZ18

## How to Test the Joystick

Testing the Analog Thumbstick may be required as the Maker who built the device would not have been able to test out the device unless they had access to an Xbox Adaptive Controller.

### Option 1: Testing the Joystick with the Gamepad Tester (for PC, iOS, or Android)

Once you have the joystick plugged in according to the steps above and the XAC is connected to the device, go to the Gamepad Tester website: https://gamepad-tester.com/. From here, you should be able to move your joystick in any direction and if the joystick on the screen moves in the same directions, it should work. If this is not the case, please contact the maker who built the device or a Makers Making Change employee.

### Option 2: Testing the Joystick by Browsing Through the Menu (Xbox)

Once you have the joystick plugged in according to the steps above, and the XAC is connected to the Xbox, you should be able to use the joystick to move up, down, left, and right through the options on the general menu. If your joystick does not work as expected, please contact the maker who built the device or a Makers Making Change employee.

## 3D Printed Base Dimensions

| Length (mm) | Width (mm) | Height (mm) | Mass (g)
Joystick Housing | 69 | 69 | 23 | 39
U-shaped Topper (if requested) | 90 | 71 | 45 | 45

## Cleaning

The Analog Joystick and 3D printed joystick topper can be wiped down with sanitizing cleaners. Do not wash the Analog Joystick in high heat as this is unsafe for electronics (i.e., do not put in the dishwasher, the washing machine, or soak in hot water).

© 2022 by Neil Squire / Makers Making Change. This work is licensed under the CC BY SA 4.0 License: http://creativecommons.org/licenses/by-sa/4.0 Files available at https://makersmakingchange.com/project/analog-thumbstick/ Page 2 of 3

V1.0 | MAY 2022 Analog Thumbstick user Quick Guide

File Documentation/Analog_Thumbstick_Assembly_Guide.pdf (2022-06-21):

V1.0 | MAY 2022

## Analog Thumbstick

## ASSEMBLY GUIDE

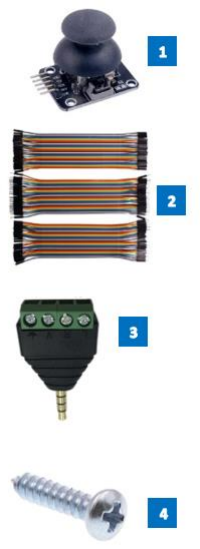
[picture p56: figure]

© 2022 by Neil Squire / Makers Making Change. This work is licensed under the CC BY SA 4.0 License: http://creativecommons.org/licenses/by-sa/4.0
Files available at | https://makersmakingchange.com/project/analog-thumbstick/ (https://makersmakingchange.com/?post_type=project&p=14952&preview=true) | Page 1 of 12
Required Components | BOM
Thumbstick without Press
Down Function
1. 1x PS2 Joystick
2. 12x Dupont Wires: 4
male/male, 4
male/female, 4
female/female – it is
| recommended that the same 4 colours are used

for the different types
of wires as they will be
getting connected.
3. 1x Headphone Adapter
4. 8x #4 1/2" screws

Thumbstick with Press Down Function

1. 1x PS2 Joystick
2. 16x Dupont Wires: 6
male/male, 5
male/female, 5
female/female – it is
recommended that the
same 5 colours are used
for the different types
of wires as they will be
getting connected.
3. 2x Headphone Adapters
4. 8x #4 1/2" screws

### Required Tools

- Small flat headed screwdriver
- Tape

### Assembly Instructions for the Analog Thumbstick without the Press Down Function – pg 2

### Assembly Instructions for the Analog Thumbstick with the Press Down Function – pg 5

Please refer to the Analog Joystick Maker Checklist to ensure you ask the user which version of the joystick they want.

## ASSEMBLY GUIDE

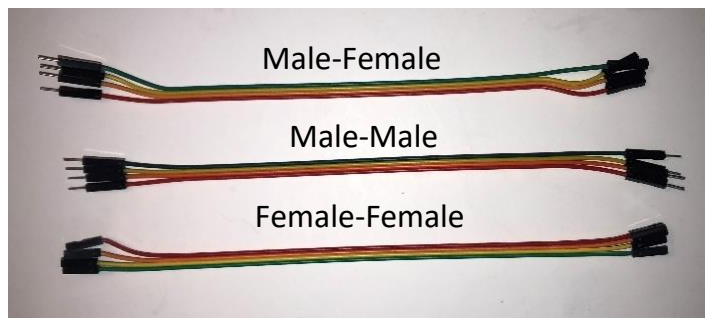
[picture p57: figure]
Male-Female; Male-Male; Female-Female
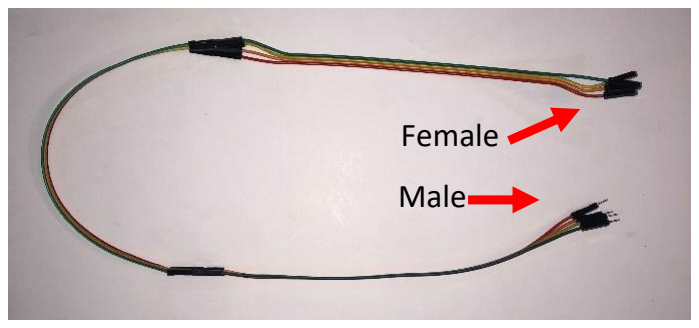
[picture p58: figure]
Male; Female
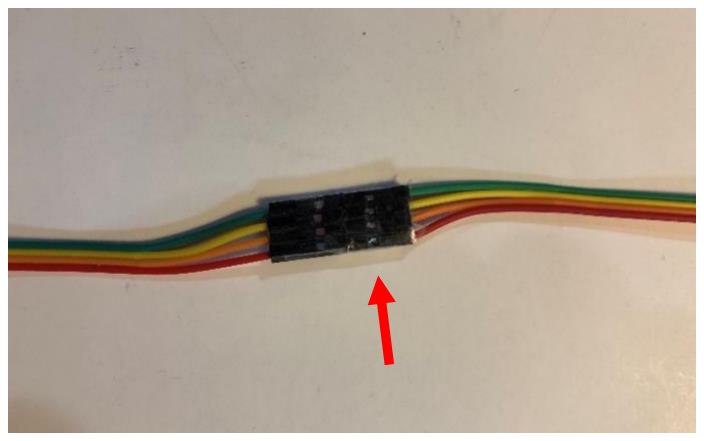
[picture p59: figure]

© 2022 by Neil Squire / Makers Making Change.

Files available at | https://makersmakingchange.com/project/analog-thumbstick/ (https://makersmakingchange.com/?post_type=project&p=14952&preview=true) | Page 2 of 12

### Assembly Instructions for Analog Thumbstick without the Press Down Function

### Step 1

Locate 12 dupont wires: 4 male – female, 4 male-male, 4 female-female. It is also recommended that you use the same colours for each of these different types of wires.

### Step 2

Connect the same colour wires so that you now have wires 3 lengths long, with one male end and one female end.

### Step 3

Use tape to secure the connected wires.

## ASSEMBLY GUIDE

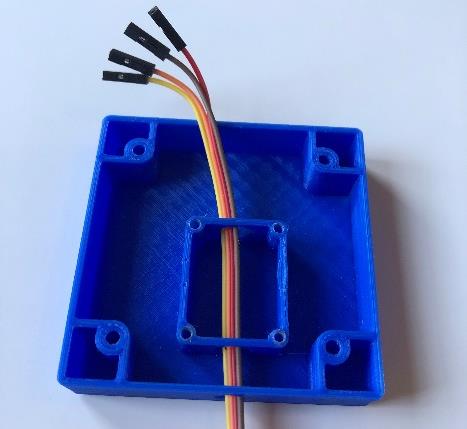
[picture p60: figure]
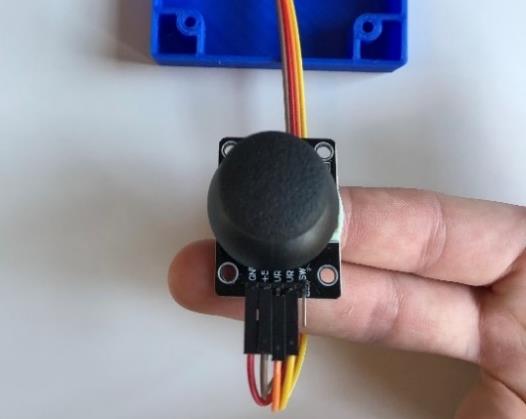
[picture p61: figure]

© 2022 by Neil Squire / Makers Making Change.

Files available at | https://makersmakingchange.com/project/analog-thumbstick/ (https://makersmakingchange.com/?post_type=project&p=14952&preview=true) | Page 3 of 12

### Step 4

Feed the female end of the wires through the 3 holes in the 3D printed joystick base.

### Step 5

Connect the wires to the GND, +5V, VRX, and VRY prongs on the joystick.

### Step 6

Connect the joystick to the 3D printed base with 4 screws.

## ASSEMBLY GUIDE

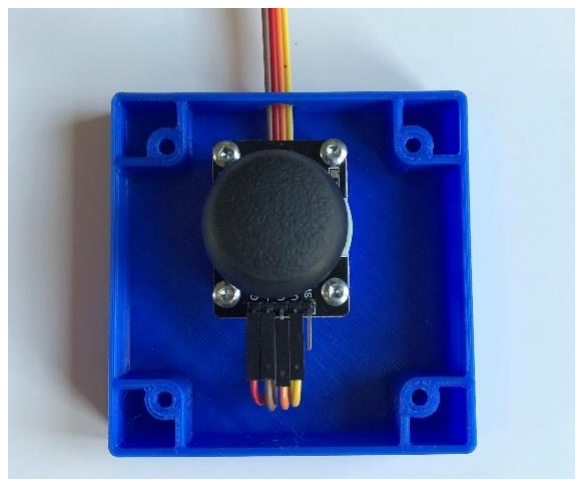
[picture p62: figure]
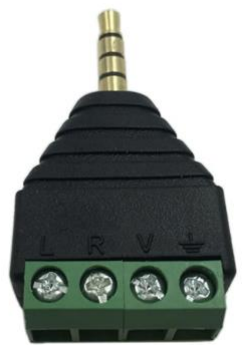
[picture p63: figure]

© 2022 by Neil Squire / Makers Making Change.

Files available at | https://makersmakingchange.com/project/analog-thumbstick/ (https://makersmakingchange.com/?post_type=project&p=14952&preview=true) | Page 4 of 12

### Step 7

Loosen the 4 screws on the headphone adapter.

### Step 8

Insert the male ends of the wires under the screws in the headphone adapter according to the diagram above. When inserted, tighten the screws to secure the wires.

## ASSEMBLY GUIDE

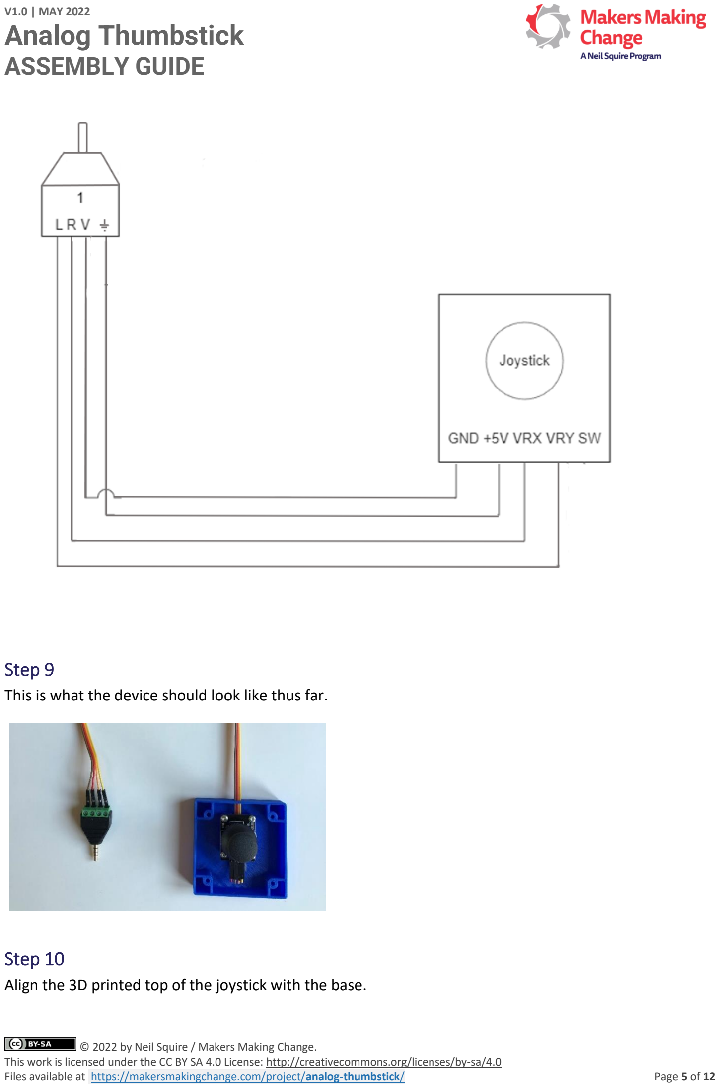
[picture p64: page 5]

© 2022 by Neil Squire / Makers Making Change.

Files available at | https://makersmakingchange.com/project/analog-thumbstick/ (https://makersmakingchange.com/?post_type=project&p=14952&preview=true) | Page 5 of 12

### Step 9

This is what the device should look like thus far.

### Step 10

Align the 3D printed top of the joystick with the base.

## ASSEMBLY GUIDE

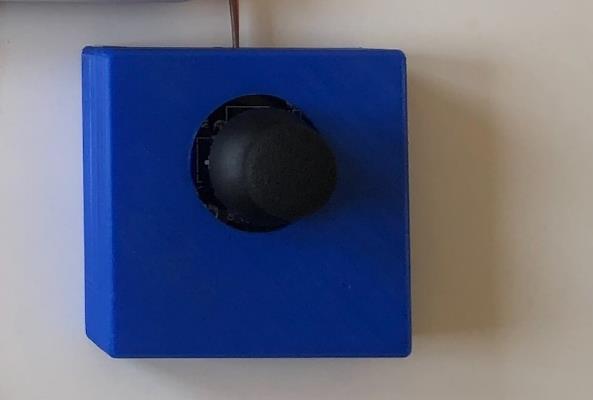
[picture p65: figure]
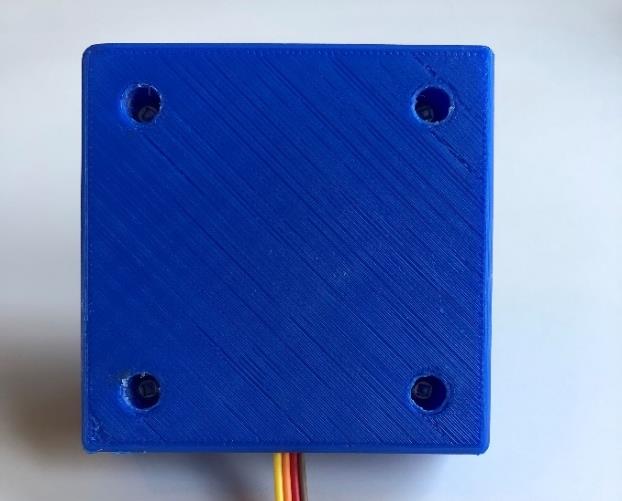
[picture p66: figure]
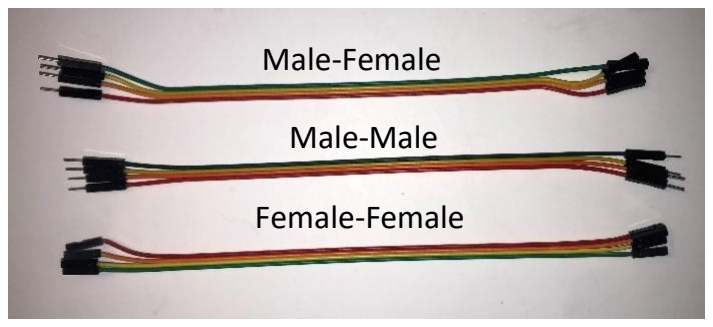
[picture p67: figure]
Male-Female; Male-Male; Female-Female

© 2022 by Neil Squire / Makers Making Change.

Files available at | https://makersmakingchange.com/project/analog-thumbstick/ (https://makersmakingchange.com/?post_type=project&p=14952&preview=true) | Page 6 of 12

### Step 11

Insert 4 screws in the base of the joystick to hold the top and base together.

### Assembly Instructions for Analog Thumbstick with the Press Down Function

### Step 1

Locate 12 dupont wires: 4 male – female, 4 male-male, 4 female-female. It is also recommended that you use the same colours for each of these different types of wires.

## ASSEMBLY GUIDE

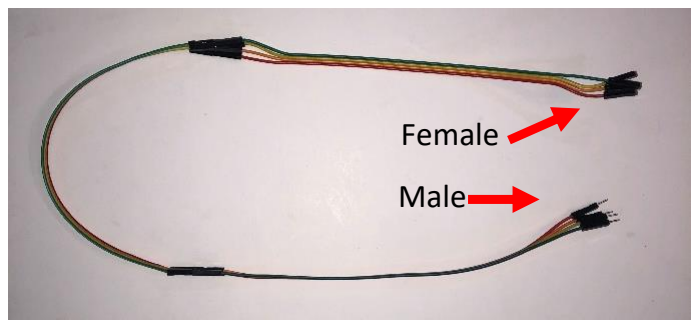
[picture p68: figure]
Male; Female
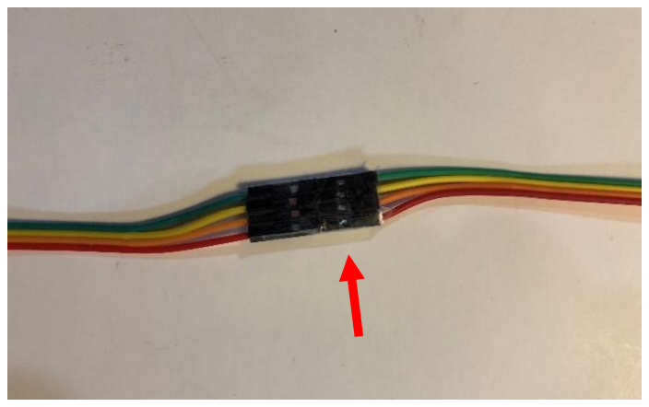
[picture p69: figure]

© 2022 by Neil Squire / Makers Making Change.

Files available at | https://makersmakingchange.com/project/analog-thumbstick/ (https://makersmakingchange.com/?post_type=project&p=14952&preview=true) | Page 7 of 12

### Step 2

Connect the same colour wires so that you now have wires 3 lengths long, with one male end and one female end.

### Step 3

Use tape to secure the connected wires.

### Step 4

Locate 3 more dupont wires: 1 male – female, 1 male-male, 1 and 1 female-female of the same colour. Connect and tape them to each other similar to steps 2 and 3.

### Step 5

Feed the female end of the 5 wires through the 3 holes in the 3D printed joystick base.

## ASSEMBLY GUIDE


© 2022 by Neil Squire / Makers Making Change.

Files available at | https://makersmakingchange.com/project/analog-thumbstick/ (https://makersmakingchange.com/?post_type=project&p=14952&preview=true) | Page 8 of 12

### Step 6

Connect the group of 4 wires to the GND, +5V, VRX, and VRY prongs on the joystick. Connect the single 5th wire to the SW prong.

### Step 7

Connect the joystick to the 3D printed base with 4 screws.

## ASSEMBLY GUIDE


© 2022 by Neil Squire / Makers Making Change.

Files available at | https://makersmakingchange.com/project/analog-thumbstick/ (https://makersmakingchange.com/?post_type=project&p=14952&preview=true) | Page 9 of 12

### Step 8

Loosen the 4 screws on both of the headphone adapters.

### Step 9

Insert the male ends of the wires under the screws in the headphone adapters according to the diagram above. This will also require a single male-male Dupont wire to be used as shown above in addition to previously mentioned wires. When inserted, tighten the screws to secure the wires. Note: on headphone adapter 1, 2 wires will be going into the V port. This may be challenging but both wires should be able to be secured with one screw.

## ASSEMBLY GUIDE

Single male-male Dupont wire; Wire from Step 4

© 2022 by Neil Squire / Makers Making Change.

Files available at | https://makersmakingchange.com/project/analog-thumbstick/ (https://makersmakingchange.com/?post_type=project&p=14952&preview=true) | Page 10 of 12

### Step 10

This is what the device should look like thus far.

Wires from Step 2

## ASSEMBLY GUIDE


© 2022 by Neil Squire / Makers Making Change.

Files available at | https://makersmakingchange.com/project/analog-thumbstick/ (https://makersmakingchange.com/?post_type=project&p=14952&preview=true) | Page 11 of 12

### Step 11

Align the 3D printed top of the joystick with the base.

### Step 12

Insert 4 screws in the base of the joystick to hold the top and base together.

## ASSEMBLY GUIDE

© 2022 by Neil Squire / Makers Making Change.

Files available at | https://makersmakingchange.com/project/analog-thumbstick/ (https://makersmakingchange.com/?post_type=project&p=14952&preview=true) | Page 12 of 12

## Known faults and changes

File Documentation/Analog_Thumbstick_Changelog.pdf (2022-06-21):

V1.0 MAY 2022

# Analog Thumbstick

# CHANGELOG

© 2022 by Neil Squire / Makers Making Change. This work is licensed under the CC BY SA 4.0 License: http://creativecommons.org/licenses/by-sa/4.0
Files available at | https://makersmakingchange.com/project/analog-thumbstick/ (https://makersmakingchange.com/?post_type=project&p=14952&preview=true) | Page 1 of 1

# Version 1.0 | Date 05/31/2022

## - Initial version

- 3D printed joystick housing designed by Kerilyn Kennedy - Makers Making Change, inspired by Ron Nelson’s Slider enclosure.
- Documentation created by Neil Squire / Makers Making Change.
